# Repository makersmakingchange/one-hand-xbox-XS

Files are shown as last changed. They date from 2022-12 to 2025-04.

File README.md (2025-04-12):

<!--- Open Source Assistive Technology: GitHub Readme Template  --->

<!--- TITLE --->
 # One Handed Modification for Xbox Series X|S Controller

<!--- SUMMARY: A brief summary of the project. What it does, who it is for, how much it costs. --->
The one handed modification for the Xbox Series X|S Controller are modifications to allow users to operate an Xbox Series X|S controller with one hand. There are different modifications available for both right- and left-handed use.

The original design was created by [Akaki](https://www.printables.com/social/106360-akaki/about).

<!--- PHOTO --->
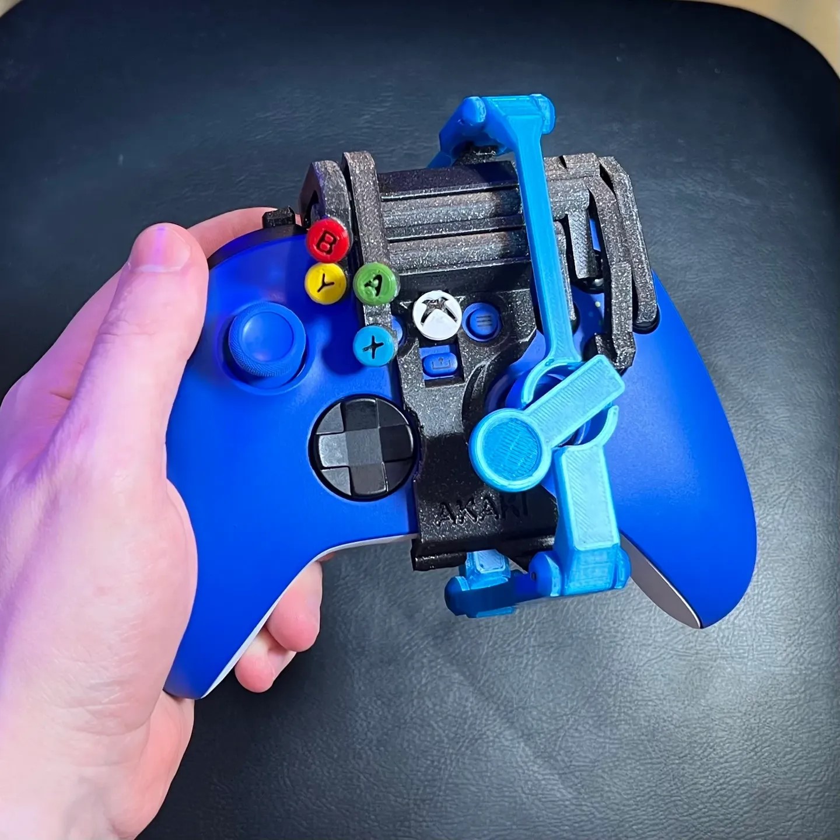
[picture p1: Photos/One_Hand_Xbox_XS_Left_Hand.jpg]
An Xbox controller with the left hand modification and Button Decorations being held in a left hand.
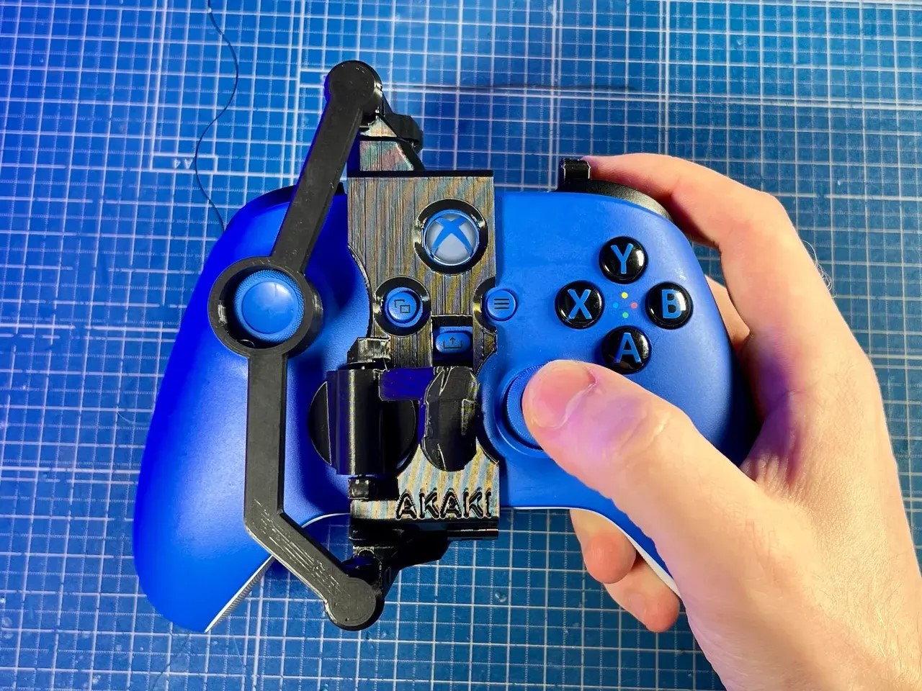
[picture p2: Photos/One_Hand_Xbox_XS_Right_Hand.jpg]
An Xbox controller with the right hand modification and Button Decorations being held in a right hand.
 

## More info at
 - [Makers Making Change Project Page](https://makersmakingchange.com/project/one-handed-mod-xbox-series-xs-controller)

## Getting Started
<!--- Include an overall idea of what major steps are required to build the device. --->

### 1. Order the Off-The-Shelf Components
The [Bill of Materials](/Documentation/OneHandedXboxXSController_BOM_V1.0.xlsx) lists all of the parts and components required to build the one handed modification for the Xbox Series X|S Controller.

### 2. Print the 3D Printable components
Select the correct modification (right or left handed modification) and print all the necessary parts for that modification.

All of the files and individual print files can be in the [/Build_Files/3D_Printing_Files](/Build_Files/3D_Printing/) folder.

### 3. Assemble the one handed modification for the Xbox Series X|S Controller.
Reference the [maker guide](/Documentation/OneHandedXboxXSController_Maker_Guide_V1.0.pdf) for the tools and steps required to build each portion.

<!---FILES: This section includes all the information and files required to build and modify the device, including documentation, design files, and build files. --->
## Files

<!--- DOCUMENTATION --->
### Documentation

| Document | Version | Link |
|----------|---------|------|
| Design Summary| 1.0 | [OneHandedXboxXSController_Summary](/Documentation/OneHandedXboxXSController_Summary.pdf) |
| Design Rationale     | 1.0 | [OneHandedXboxXSController_Design_Rationale](/Documentation/OneHandedXboxXSController_Design_Rationale.pdf) |
| Bill of Materials    | 1.0 | [OneHandedXboxXSController_BOM](/Documentation/OneHandedXboxXSController_BOM.xlsx) |
| Maker Guide      | 1.0 | [OneHandedXboxXSController_Maker_Guide](/Documentation/OneHandedXboxXSController_Maker_Guide.pdf) |
| User Guide          | 1.0 | [OneHandedXboxXSController_User_Guide](/Documentation/OneHandedXboxXSController_User_Guide.pdf)           |
| Changelog            | 1.0 | [OneHandedXboxXSController_Changelog](/Documentation/OneHandedXboxXSController_Changelog.pdf)               |

### Design Files
 - Unfortunately, no CAD files are available for this device.

### Build Files
<!--- BUILD FILES --->
 - [3D Printing Files](/Build_Files/3D_Printing)

## License
<!--- LICENSE: Choose an appropriate license. We recommend an open-source hardware compatible license. --->
Everything needed or used to design, make, test, or prepare the one handed modification for the Xbox Series X|S Controller is licensed under a Creative Commons Attribution-ShareAlike 4.0 license <https://creativecommons.org/licenses/by-sa/4.0/> (CC BY-SA 4.0).

Accompanying material such as instruction manuals, videos, and other copyrightable works that are useful but not necessary to design, make, test, or prepare the one handed modification for the Xbox Series X|S Controller are published under a Creative Commons Attribution-ShareAlike 4.0 license <https://creativecommons.org/licenses/by-sa/4.0/> (CC BY-SA 4.0).

## Attribution
<!--- ATTRIBUTION: Include any information related to the development of the design. This may include who identified the initial challenge, who contributed to the design --->

 - The original design of the [One-Handed Xbox Series XS Controller](https://www.printables.com/model/156112-one-handed-xbox-series-xs-controller) was created by [Akaki](https://www.printables.com/social/106360-akaki/about) and released with a [CC-BY-NC-SA license](http://creativecommons.org/licenses/by-nc-sa/4.0/).

 - The left handed modification was remixed by [Ryan Heitanen](https://www.printables.com/social/120065-ryan-hietanen/about).

 - Additional documentation was created by Neil Squire Society / Makers Making Change.
 - The documentation template was created by Makers Making Change and is used under a CC BY-SA 4.0 license. It is available at the following link: https://github.com/makersmakingchange/OpenAT-Template

----

<!-- ABOUT MMC START -->
## About Makers Making Change
[Makers Making Change Logo](https://www.makersmakingchange.com/)

Makers Making Change is a program of [Neil Squire](https://www.neilsquire.ca/), a Canadian non-profit that uses technology, knowledge, and passion to empower people with disabilities.

Makers Making Change leverages the capacity of community based Makers, Disability Professionals and Volunteers to develop and deliver affordable Open Source Assistive Technologies.

 - Website: [www.MakersMakingChange.com](https://www.makersmakingchange.com/)
 - GitHub: [makersmakingchange](https://github.com/makersmakingchange)
 - Bluesky: [@makersmakingchange.bsky.social](https://bsky.app/profile/makersmakingchange.bsky.social)
 - Instagram: [@makersmakingchange](https://www.instagram.com/makersmakingchange)
 - Facebook: [makersmakechange](https://www.facebook.com/makersmakechange)
 - LinkedIn: [Neil Squire Society](https://www.linkedin.com/company/neil-squire-society/)
 - Thingiverse: [makersmakingchange](https://www.thingiverse.com/makersmakingchange/about)
 - Printables: [MakersMakingChange](https://www.printables.com/@MakersMakingChange)

### Contact Us
For technical questions, to get involved, or to share your experience we encourage you to [visit our website](https://www.makersmakingchange.com/) or [contact us](https://www.makersmakingchange.com/s/contact).
<!-- ABOUT MMC END -->

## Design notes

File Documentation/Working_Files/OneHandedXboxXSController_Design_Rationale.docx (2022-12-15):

# Introduction

The One Handed Modification for the Xbox Series X|S Controller is a 3D-printed device that allows users to work an Xbox Series X|S with only one hand. This device may benefit users with only one hand, or limited mobility/dexterity in one of their hands. The device will fit Xbox Series X|S controllers.

# Research

## Xbox Adaptive Controller

The Xbox Adaptive Controller (XAC) allows players with limited mobility to customize their gaming setup for the Xbox with different switches and joysticks. Users can customize the XAC to map various functions to different switches, buttons, and joysticks to suit their needs. Although this option may be preferable for some users, it is expensive and requires users to purchase and customize other devices to use properly.

## One Handed Controller Modifications

There are one handed controller modifications available for purchase or DIY. Commercially available modified controllers are typically permanently modified and more expensive than standard controllers. Other DIY options may be difficult for makers and users to create and customize.

# Requirements

## Goals

G01 | Allow people to effectively use an Xbox Series X|S controller with one hand.
G02 | Help people with one hand and/or limited mobility/dexterity in one hand play video games.

## Functional Requirements

F01 | Must fit Xbox Series X|S controllers.
F02 | Must allow players to use the controller with one hand.

## Non-functional Requirement

NF01 | Must be easy to clean.

## Constraints

C01 | Must be printable on standard maker 3D printers.

# Version 1.0

Initial designs by Akaki (https://www.printables.com/social/106360-akaki/about) and Ryan Hietanen (https://www.printables.com/social/120065-ryan-hietanen/about) are licensed under Creative Commons (4.0 International License) Attribution – Non-Commercial – Share Alike (https://creativecommons.org/licenses/by-nc-sa/4.0/).

## Right handed version 1.0

This design consists of a single .stl file that contains multiple parts. The parts are listed below:

- Thumb-stick mover
- Linkage pieces
- Leg strap/shoe holder
- Mount
- Trigger button pusher
- D-pad pusher
- Leg strap attachment

## Left handed version 1.0

This design consists of a single .stl file that contains multiple parts. The parts are listed below:

- Thumb-stick mover
- Linkage pieces
- Leg strap/shoe holder
- Mount
- Trigger button pushers
- Face button pushers
- Leg strap attachment

## Optional Parts

The below parts are optional and can be found in their own .stl files.

- Shoe (replaces leg mount)
- Button decorations

# Opportunities for Improvement

- Add a cutout to allow users to easily access the USB-C power port at the back of the controller while using the device
- Split .stl files out into individual components to facilitate replacing parts or printing parts in different colours

© 2022 by Neil Squire. This work is licensed under the CC BY SA 4.0 License: http://creativecommons.org/licenses/by-sa/4.0 Files available at https://makersmakingchange.com/project/one-handed-mod-xbox-series-xs-controller Page 1 of 1

V1.0 | December 2022 One Handed Modification for The Xbox Series X|S Controller Design Rationale

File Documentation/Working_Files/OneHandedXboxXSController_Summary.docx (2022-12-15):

# Title

One Handed Modification for the Xbox Series X|S Controller

## Subtitle

The one handed modification for the Xbox Series X|S Controller are modifications to allow users to operate an Xbox Series X|S controller with one hand. There are modifications for the right and left hands.

## Device Specifications

Build Time:

< 1hr

1-4 hr

5-10hr

>10hr

Cost:

$0 - $10

$11 - $25

$26 - $50

$51 - $100

$101 - $250

$250+

Stage: Recently Added

Skills: 3D printing

Need: Agility/Dexterity

Disability: Mobility/Physical

Difficulty: Beginner

License: Attribution – Non-commercial – Share Alike 4.0 International

Usages: Recreation and Leisure

Type: Gaming

Designer: Akaki (https://www.printables.com/social/106360-akaki/about)

Left handed design remixed by: Ryan Hietanen (https://www.printables.com/social/120065-ryan-hietanen/about)

## Device Details

### Overview

This inexpensive 3D printed modification for the Xbox Series X|S controller will allow for the user to operate their Xbox Series X|S controller with one hand. This controller adaptation makes it easier for someone who may have a difficult time holding a controller with both hands, or has greater dexterity with one hand than the other.

### Usage

This controller adaptation allows for the user to operate their Xbox Series X|S controller with only one hand. For a left handed controller, the right joystick is used by moving the whole controller. By moving the controller, the 3D printed parts enable the joystick to move simultaneously. In addition, the right shoulder buttons are migrated to the left side so all four shoulder buttons can be used with the index finger. Similarly, four 3D printed arms are used to allow the user to press the A, B, X, Y, and home buttons from the left side.

There are two different attachments for the bottom of the controller shown below that can be used depending on whether the user chooses to strap the controller to their leg (right), or can rest it on their lap or a surface of their choice using the "shoe" (left).

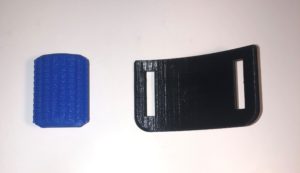
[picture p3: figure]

### Cost

The right handed modification costs $2.65 to produce and the left handed modification costs $3.00.

### Build Instructions

A set of instructions for creating this modification for the Xbox Series X|S controller can be found on the Prusa Printers website. There is a video tutorial showing the assembly of both the right and left handed versions linked here (https://www.youtube.com/watch?v=QOOU2KnhcHA).

The Xbox Series X|S controller is asymmetrical, so this modification has different files for the left and right handed modifications.

#### Skills Required

3D printing.

#### Time Required

3D printing time:

Right handed modification: 8.75-9.95 hours

Left handed modification: 10.9-12.2 hours

Assembly: 0.5-1.5 hours

#### Tools

- Flush cutters or scissors
- Sandpaper (optional)
- Superglue (optional)
- Drill and 5/64” drill bit (optional)

#### Components

- Rubber bands (optional)
- 1.75 mm 3D printer filament for pin joints

#### 3D Printing

Right Handed Modification | Left Handed Modification
Thumb-stick mover armature | Thumb-stick mover armature
Trigger pusher | Trigger pusher
Leg strap attachment | Leg strap attachment
Linkage pieces | Linkage pieces
Leg strap/shoe holder | Leg strap/shoe holder
D-pad pusher | B, A, X, Y face button pushers
Mount | Mount
Shoe (optional) | Shoe (optional)
Button decorations (optional) | Button decorations (optional)

### Design

### Attribution

Original design: Akaki (https://www.printables.com/social/106360-akaki/about)

Left handed design remixed by: Ryan Hietanen (https://www.printables.com/social/120065-ryan-hietanen/about)

© 2022 by Neil Squire. This work is licensed under the CC BY SA 4.0 License: http://creativecommons.org/licenses/by-sa/4.0 Files available at https://makersmakingchange.com/project/one-handed-mod-xbox-series-xs-controller Page 1 of 2

V1.0 | December 2022 One Handed Modification for The Xbox Series X|S Controller Summary

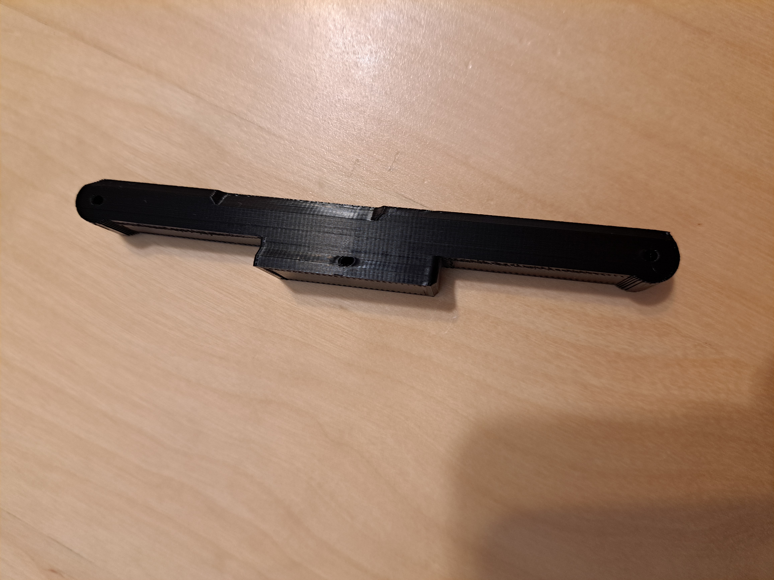
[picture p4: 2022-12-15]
Photos/right handed modification/Holder first side.jpg

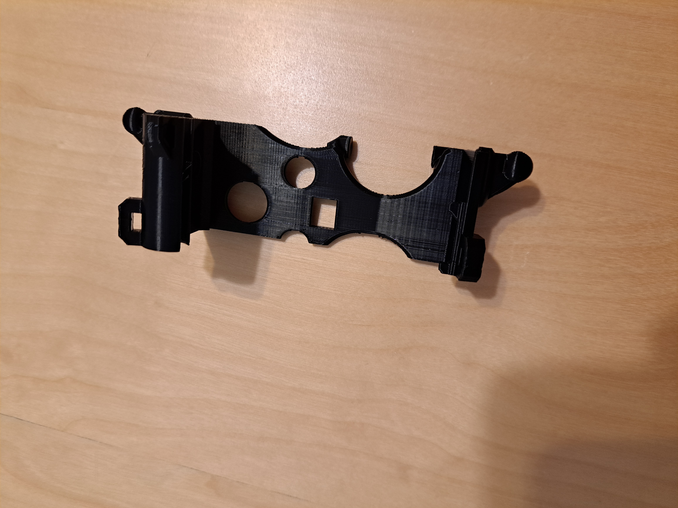
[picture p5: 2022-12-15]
Photos/right handed modification/Mount bottom.jpg

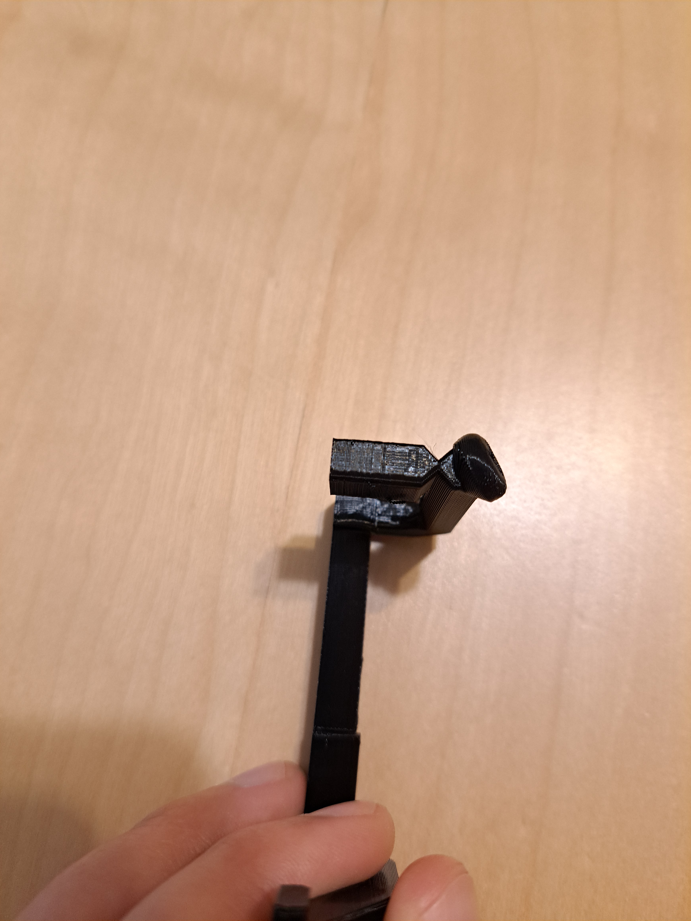
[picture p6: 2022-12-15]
Photos/left handed modification/A Button front.jpg

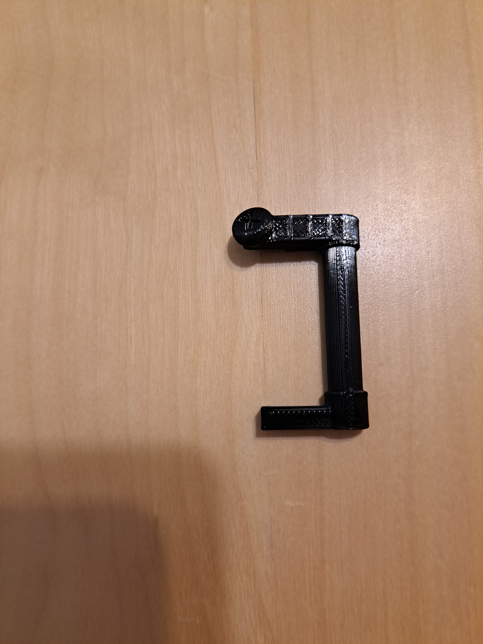
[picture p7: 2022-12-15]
Photos/left handed modification/X Button top.jpg

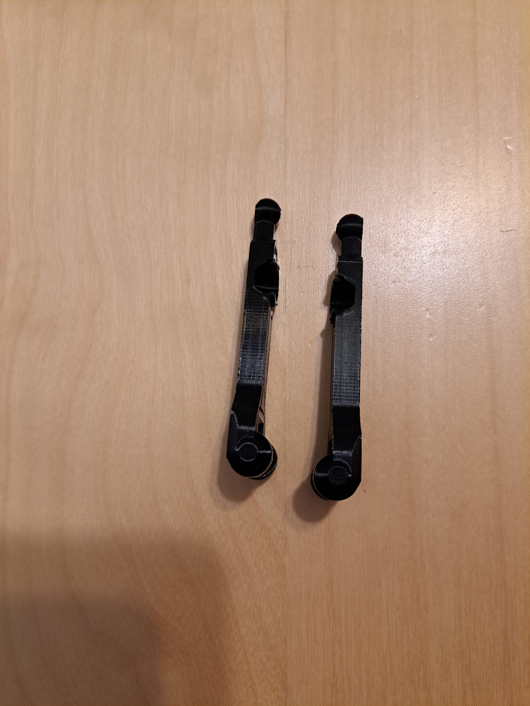
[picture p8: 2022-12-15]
Photos/right handed modification/Linkages side.jpg

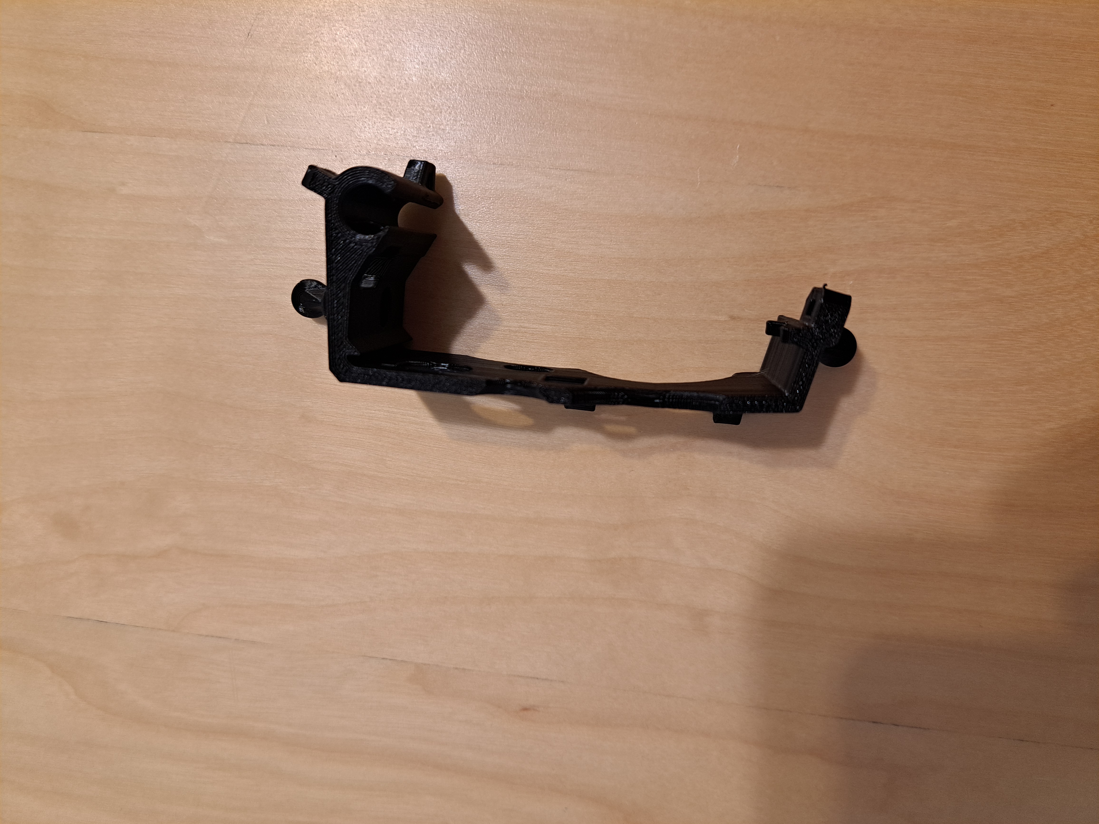
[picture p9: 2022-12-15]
Photos/right handed modification/Mount first side.jpg

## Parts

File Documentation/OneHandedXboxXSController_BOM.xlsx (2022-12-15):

Device: One Handed Modification for the Xbox Series X|S Controller |  |  | Total Cost | Total Print time (hr) | Total filament (g)
Version: V1.0 | Date Created: 11/20/2022 | Right handed | $2.65 | 9.95 | 64
Commercial Parts: |  | Left Handed | $3.00 | 12.20 | 78
Part type (Electrical. Mechanical, Sanitization, ect) | Part Name | Quantity Needed | Pkg Quantity | Price per package | Price per Unit | Price for qty needed | Link
Mechanical | Rubber bands (optional) | 5 | 600 | $13.99 | $0.02 | $0.12 | https://www.amazon.ca/stores/page/89A25064-42E4-458E-873D-0079F105D03D/?store_ref=SB_A0645920QPZJJP4FNBW2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
Mechanical | Hook and loop strap | 1 | 16 | $14.99 | $0.94 | $0.94 | https://www.amazon.ca/TamBee-Organizer-Reusable-Adjustable-Fastener/dp/B0B77CNTPH?hvadid=620922523376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
3D Printed Parts ESTIMATED PRICING USING 1KG ROLL COST: | $25.00
Part | Description | Quantity Needed | TOTAL Mass (g) | Estimated Price | Print Time (Min) | Link
Right handed modification | Right hand uses the controller | 1 | 55 | $1.38 | 525
Left handed modification | Left hand uses controller | 1 | 68 | $1.70 | 656
Button decorations (optional for Left handed modification, not used for right handed modification) | Make A, B, X, Y, and Xbox buttons different colour | 1 | 1 | $0.03 | 4
Shoe (optional) | Replaces leg strap | 1 | 9 | $0.22 | 72
 |  |  |  | $0.00
 |  |  | Total Print Cost: | $3.33
Tools for Assembly
1.75 mm 3D printer filament for pinned joints
Flush cutters
5/64" drill bit (optional)
Drill (optional)
Alternatives (if there are other sources for some parts link them below)
Part and description | Link

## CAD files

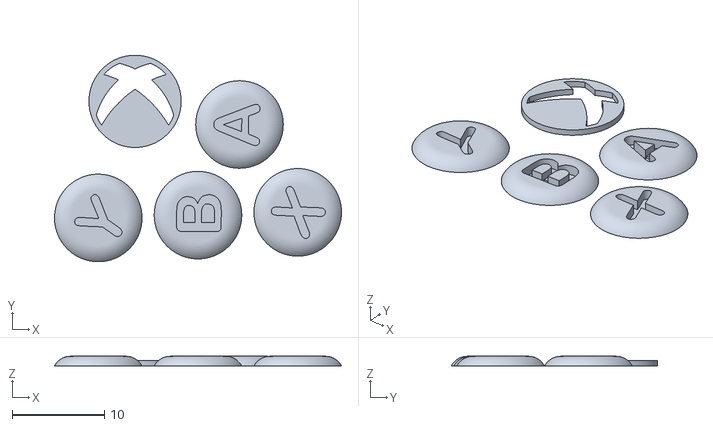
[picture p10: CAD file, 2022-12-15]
Build_Files/3D_Printing_Files/button decorations.stl
31.1 x 22.4 x 1.04

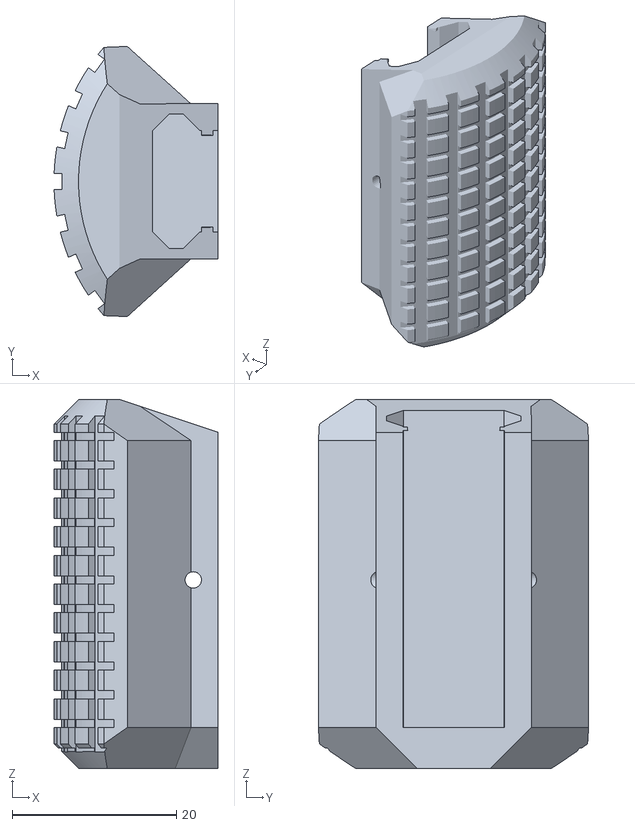
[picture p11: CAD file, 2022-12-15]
Build_Files/3D_Printing_Files/shoe.stl
20.0 x 33.0 x 45.0

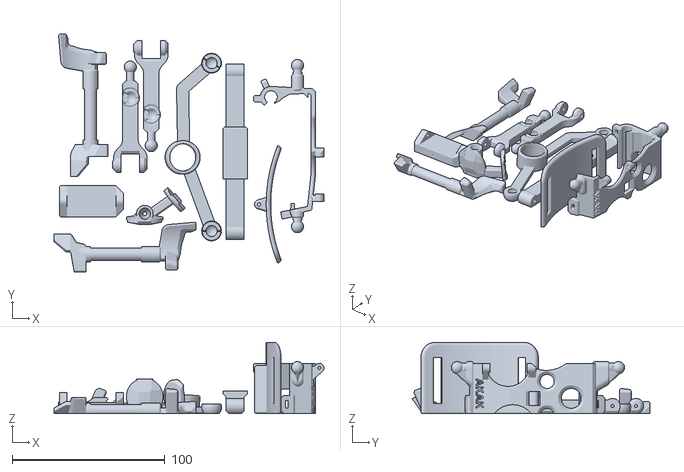
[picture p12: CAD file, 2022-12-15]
Build_Files/3D_Printing_Files/right handed xbox v1.stl
177.0 x 155.8 x 46.8

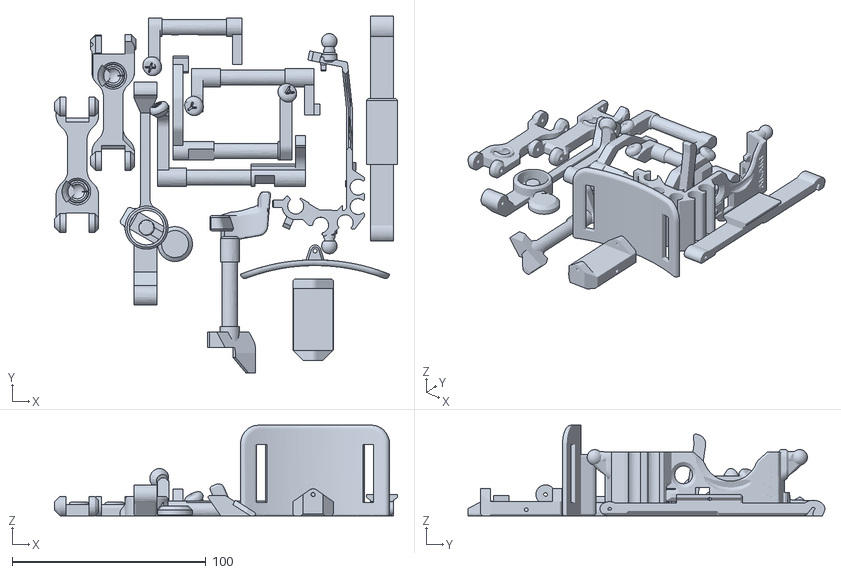
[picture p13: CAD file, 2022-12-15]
Build_Files/3D_Printing_Files/left-handed-xbox-Series X_S controller.stl
176.8 x 183.9 x 46.8

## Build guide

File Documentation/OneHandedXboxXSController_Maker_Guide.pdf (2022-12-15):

V1.0 | December 2022

# One Handed Modification for the Xbox Series X|S Controller

## MAKER GUIDE

© 2022 by Neil Squire (https://www.neilsquire.ca/)
This work is licensed under the CC BY SA 4.0 License: http://creativecommons.org/licenses/by-sa/4.0 Files available at https://makersmakingchange.com/project/one-handed-mod-xbox-series-xs-controller

### Overview

This document contains the necessary information to build a one handed modification for the Xbox Series X|S Controller.

### Contents

Step 1 | Error! Bookmark not defined.
Step 2 | Error! Bookmark not defined.
Step 3 | Error! Bookmark not defined.

# One Handed Modification for the Xbox Series X|S Controller

## MAKER GUIDE

© 2022 by Neil Squire (https://www.neilsquire.ca/)

### Maker Checklist

This list provides an overview of the steps required to build and deliver the device.

### Maker To Do List

Read through the Assembly Guide to become familiar with required components, tools, supplies, and safety gear and overall assembly steps.
Talk to User about customization options (e.g., colour, shoe vs leg strap, hook and loop strap size, etc.)
Gather tools, supplies, and safety equipment.
Assemble the device
Test device
Print “User Quick Guide”

### Items to Give to User

Assembled, tested device
“User Quick Guide”

### Tool List

Flush cutters or scissors
Sandpaper (optional)
Superglue (optional)
Drill and 5/64” drill bit (optional)

# One Handed Modification for the Xbox Series X|S Controller

## MAKER GUIDE

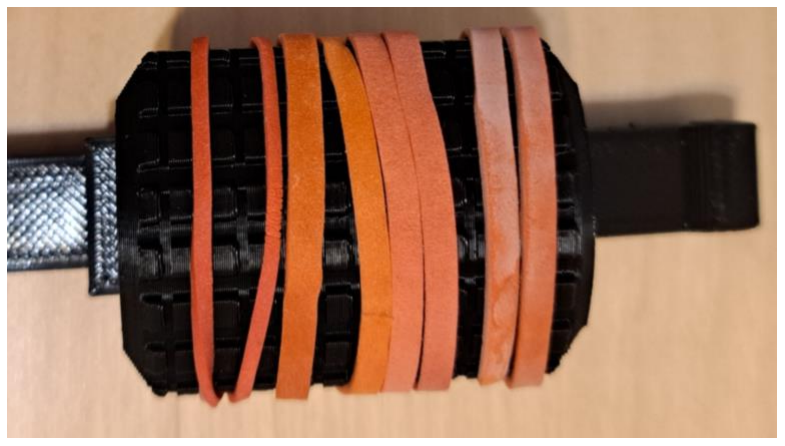
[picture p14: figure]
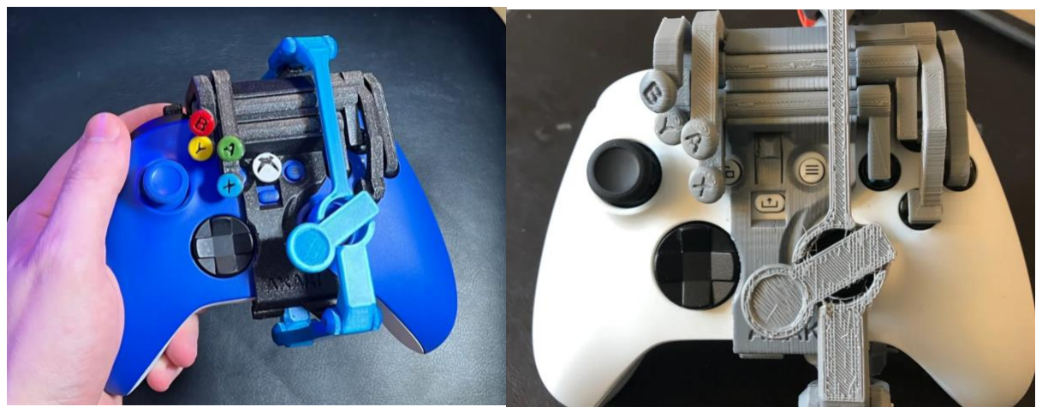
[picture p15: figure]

© 2022 by Neil Squire (https://www.neilsquire.ca/)

### Customization Guide

The user may request the “shoe” or leg strap for controlling the joystick of the unused hand. If the user requests the “shoe”, the original designer recommends printing it with TPU is possible. If printing in TPU is not possible, we recommend adding rubber bands around the “shoe” to increase grip, as shown below.

If the user requests the left handed modification, you may add the Button Decorations, ideally in a different colour from the rest of the device for colour contrast. The Button Decorations are a separate .slt file and include A, B, X, Y, and the Xbox logo. The controller with and without the Button Decorations is shown below.

# One Handed Modification for the Xbox Series X|S Controller

## MAKER GUIDE

© 2022 by Neil Squire (https://www.neilsquire.ca/)

### 3D Printing Guide

Note that all components can be printed without supports as the designer built supports into the design where necessary.

### 3D Printing Summary

Metrics | Right Handed Modification | Left Handed Modification | Button Decorations | Shoe
Total Print Time (min) | 525 (8.75 hours) | 656 (10.9 hours) | 4 (0.07 hours) | 72 (1.2 hours)
Total Number of Components | 10 | 12 | 5 | 1
Typical Total Mass (g) | 55 | 68 | <1 | 9
Typical Number of Print Setups | 1 | 1 | 1 | 1

### 3D Printing Settings

Print File Name | Qty | Total Print Time (hr:min) | Mass (g) | Infill (%) | Support(Y/N) | Layer Height/ Nozzle Diameter(mm) | Notes (orientation, special settings, etc.)
right handed xbox v1.stl | 1 | 8:45 | 55 | 20 | N | 0.2/0.4
left-handed-xbox-Series X_S controller.stl | 1 | 10:56 | 68 | 20 | N | 0.2/0.4
shoe.stl | 1 | 1:12 | 9 | 20 | N | 0.2/0.4 | -Optional print to replace leg strap - Can be printed in TPU if available
button decorations.stl | 1 | 0:04 | <1 | 20 | N | 0.2/0.4 | -Optional print

### Post-Processing

Remove any print helpers and built-in supports on the components.

# One Handed Modification for the Xbox Series X|S Controller

## MAKER GUIDE

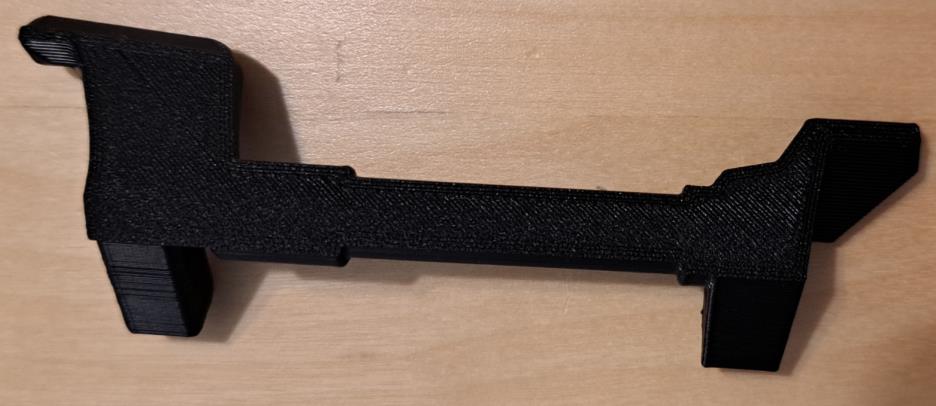
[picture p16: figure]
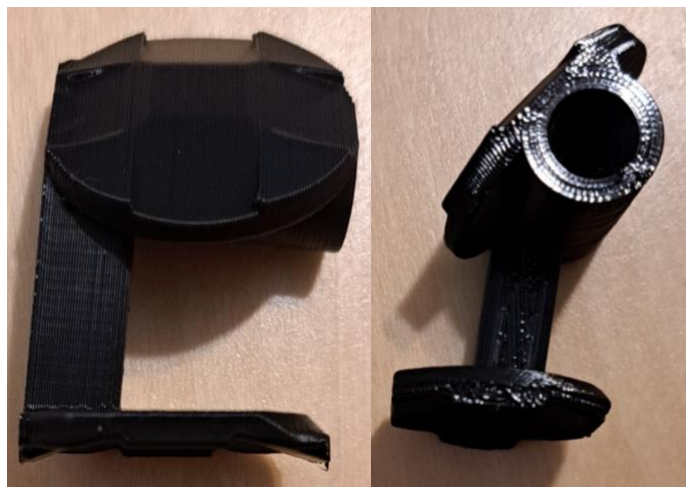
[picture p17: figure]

© 2022 by Neil Squire (https://www.neilsquire.ca/)

### Examples of Quality Prints

The following pictures show examples of quality prints for each component required for the controller modifications.

### Right Hand Modification

Trigger Pusher

D-Pad Pusher

# One Handed Modification for the Xbox Series X|S Controller

## MAKER GUIDE

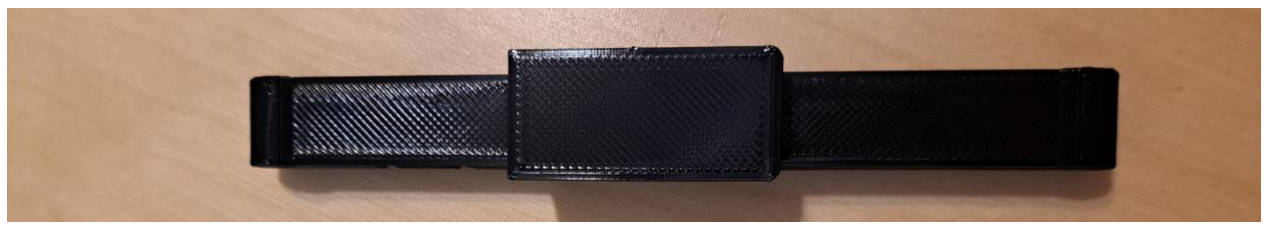
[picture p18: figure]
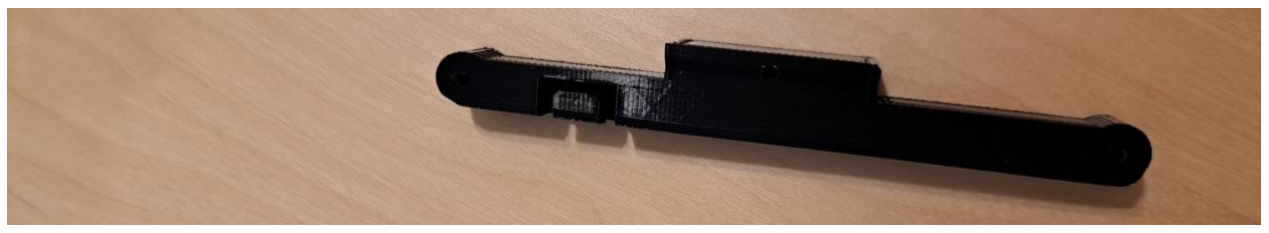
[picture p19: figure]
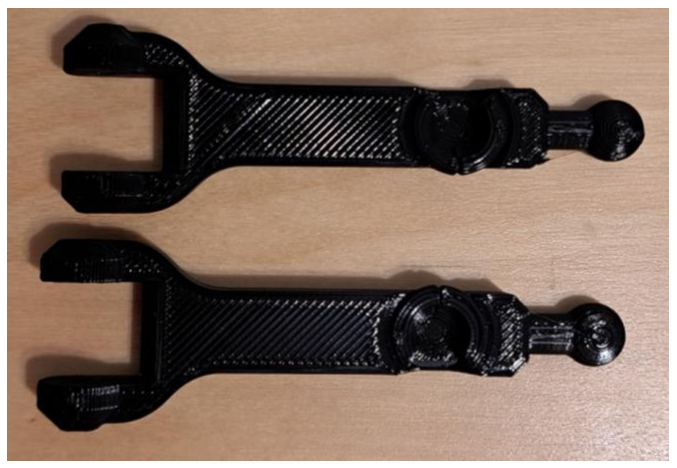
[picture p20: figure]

© 2022 by Neil Squire (https://www.neilsquire.ca/)

Leg Strap/Shoe holder

Linkage Pieces

# One Handed Modification for the Xbox Series X|S Controller

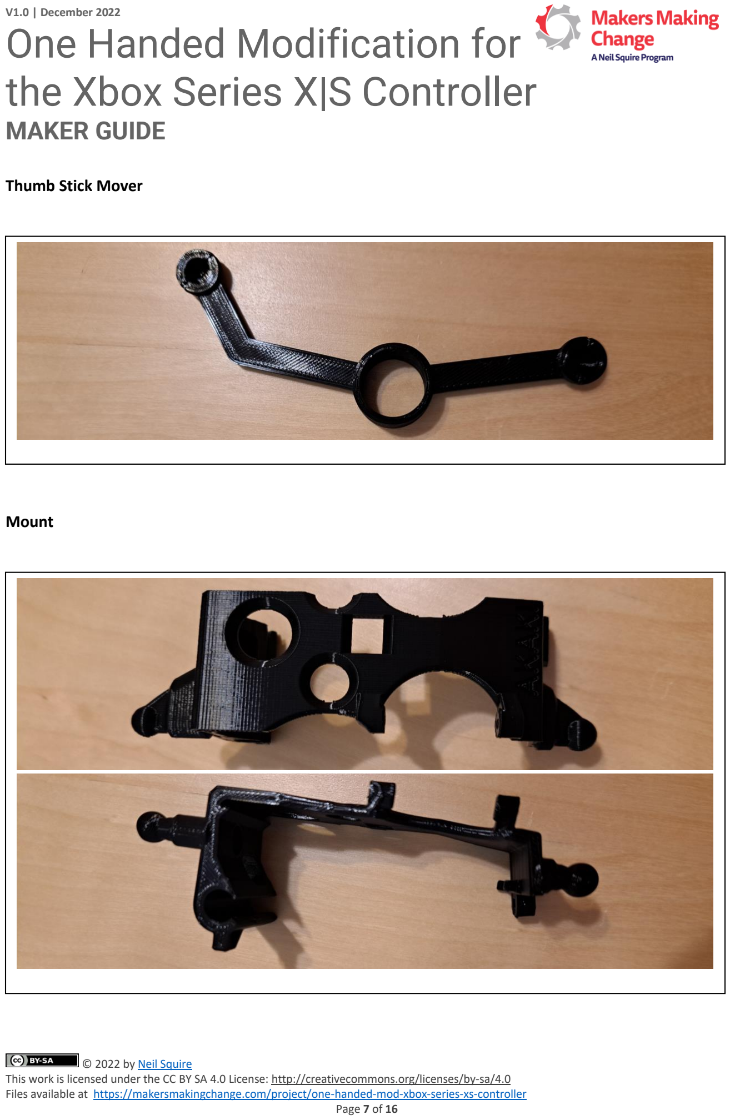
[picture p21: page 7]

## MAKER GUIDE

© 2022 by Neil Squire (https://www.neilsquire.ca/)

Thumb Stick Mover

Mount

# One Handed Modification for the Xbox Series X|S Controller

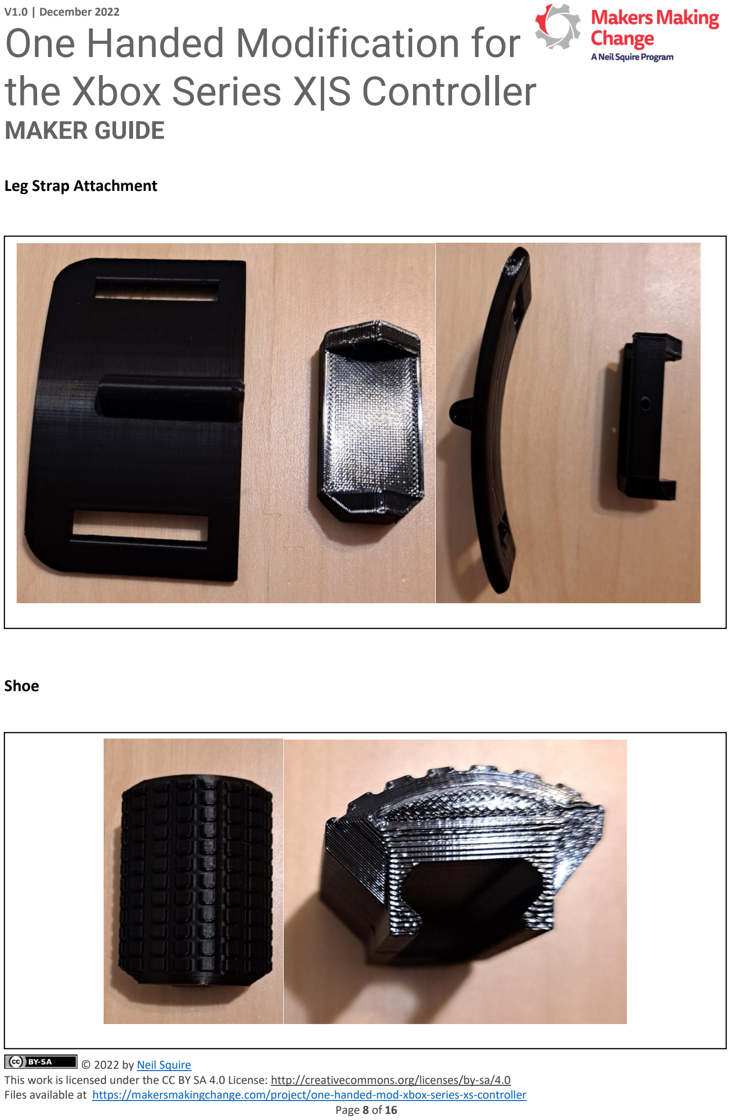
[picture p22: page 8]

## MAKER GUIDE

© 2022 by Neil Squire (https://www.neilsquire.ca/)

Leg Strap Attachment

Shoe

# One Handed Modification for the Xbox Series X|S Controller

## MAKER GUIDE

© 2022 by Neil Squire (https://www.neilsquire.ca/)

Button Decorations

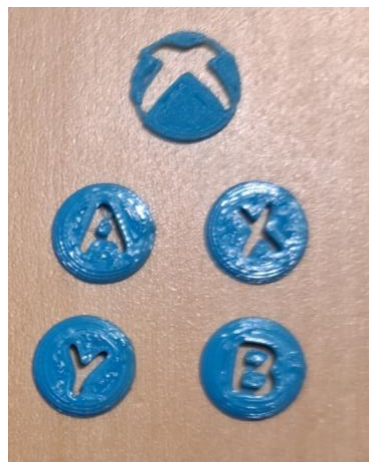
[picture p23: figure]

# One Handed Modification for the Xbox Series X|S Controller

## MAKER GUIDE

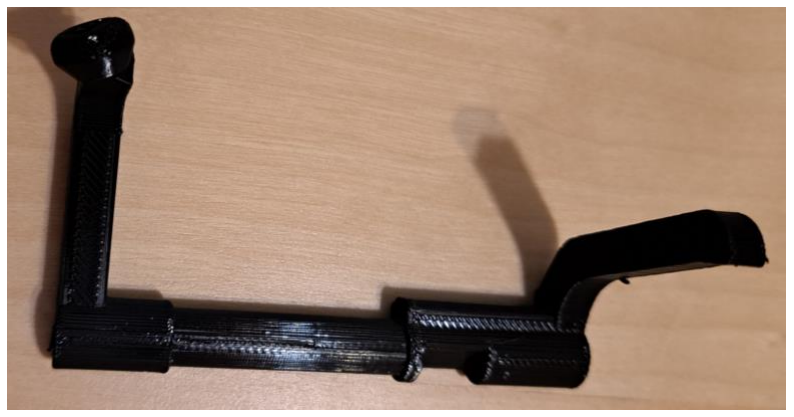
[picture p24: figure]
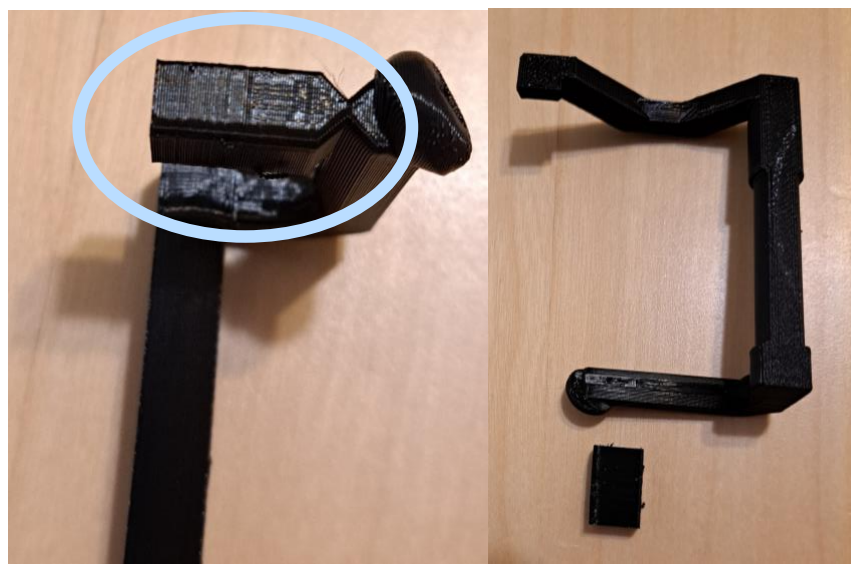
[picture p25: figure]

© 2022 by Neil Squire (https://www.neilsquire.ca/)

### Left Handed Modification

The left handed modification also includes the trigger pusher, leg strap/shoe holder, leg strap attachment/shoe, and optional button decorations. These parts are the same as those for the right handed modification.

B Button Pusher

A Button Pusher

# One Handed Modification for the Xbox Series X|S Controller

## MAKER GUIDE

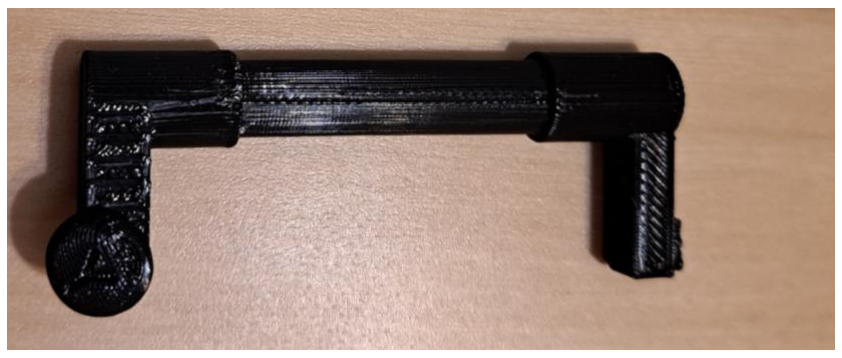
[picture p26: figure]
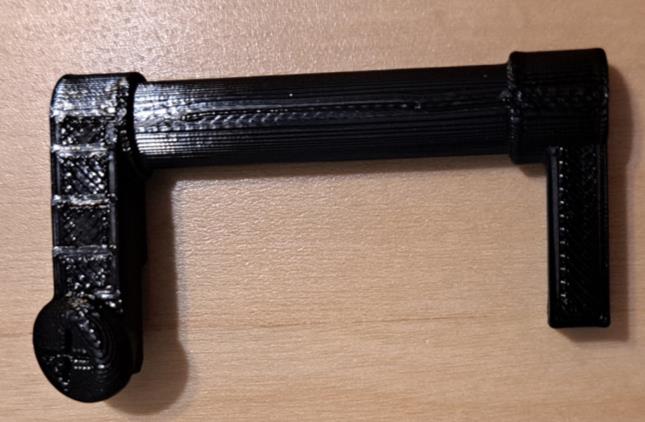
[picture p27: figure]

© 2022 by Neil Squire (https://www.neilsquire.ca/)

The A Button pusher has a built-in support, which is circled in the first picture. The support must be snapped off, and it comes off easily. The break should be clean, as seen in the last picture above.

Y Button Pusher

X Button Pusher

# One Handed Modification for the Xbox Series X|S Controller

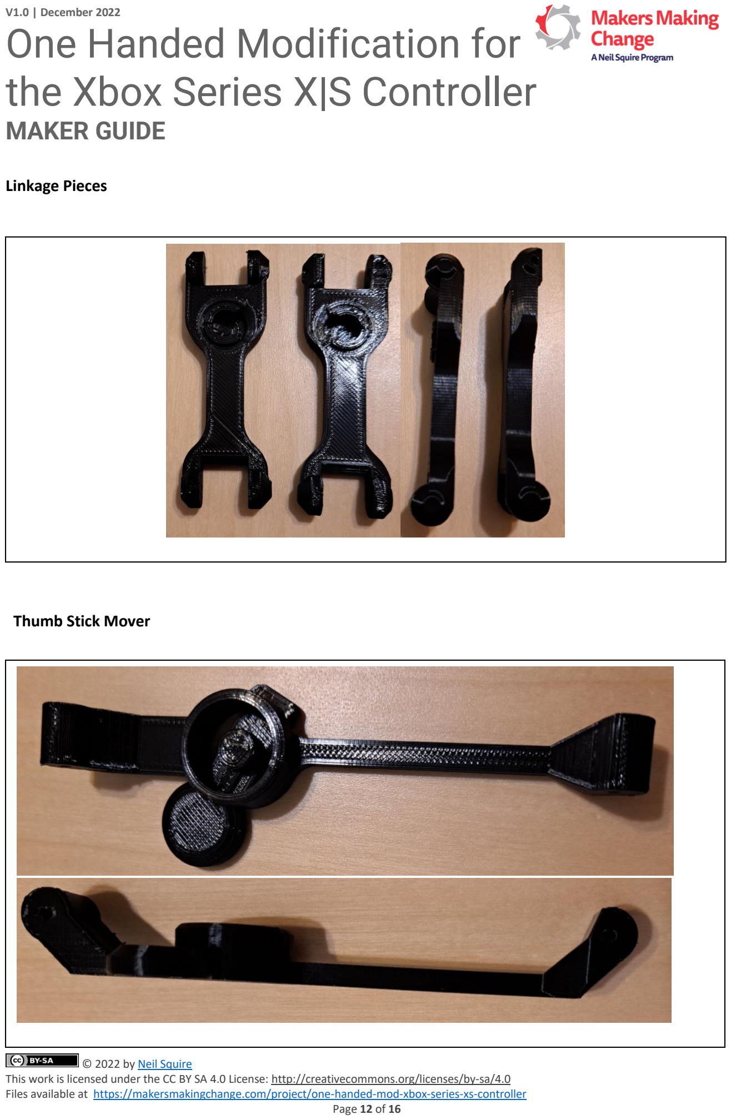
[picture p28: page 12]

## MAKER GUIDE

© 2022 by Neil Squire (https://www.neilsquire.ca/)

Linkage Pieces

Thumb Stick Mover

# One Handed Modification for the Xbox Series X|S Controller

## MAKER GUIDE

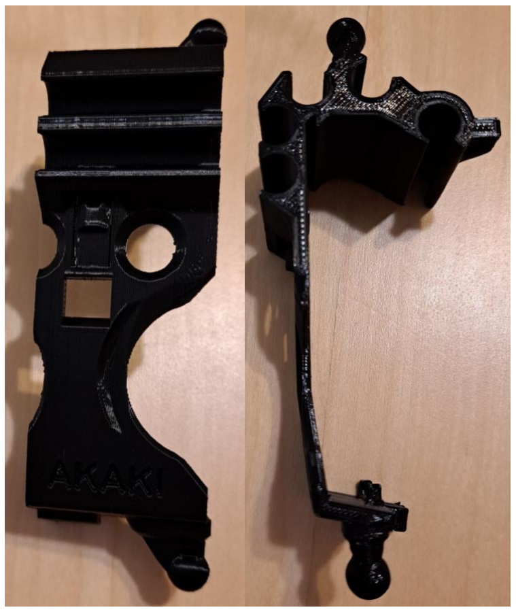
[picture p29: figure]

© 2022 by Neil Squire (https://www.neilsquire.ca/)

Mount

# One Handed Modification for the Xbox Series X|S Controller

## MAKER GUIDE

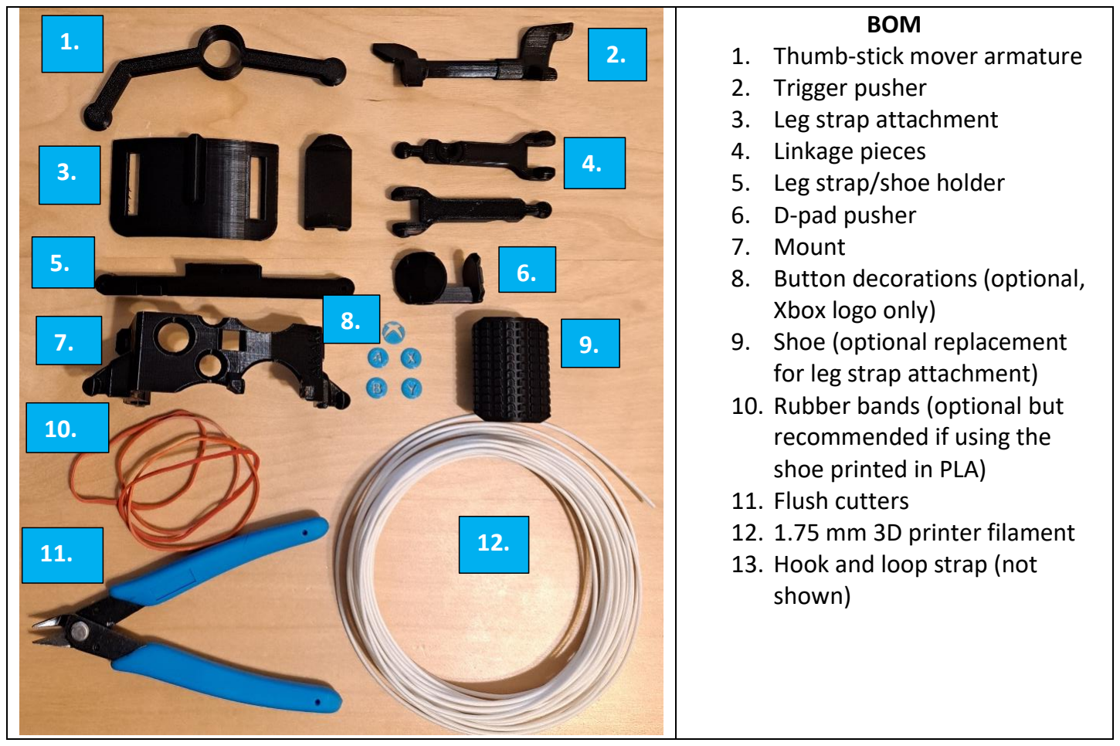
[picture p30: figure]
BOM 1. Thumb-stick mover armature 2. Trigger pusher 3. Leg strap attachment 4. Linkage pieces 5. Leg strap/shoe holder 6. D-pad pusher 7. Mount 8. Button decorations (optional, Xbox logo only) 9. Shoe (optional replacement for leg strap attachment) 10. Rubber bands (optional but recommended if using the shoe printed in PLA) 11. Flush cutters 12. 1.75 mm 3D printer filament 13. Hook and loop strap (not shown)

© 2022 by Neil Squire (https://www.neilsquire.ca/)

### Assembly Guide

### Required Components

Right Handed Modification

# One Handed Modification for the Xbox Series X|S Controller

## MAKER GUIDE

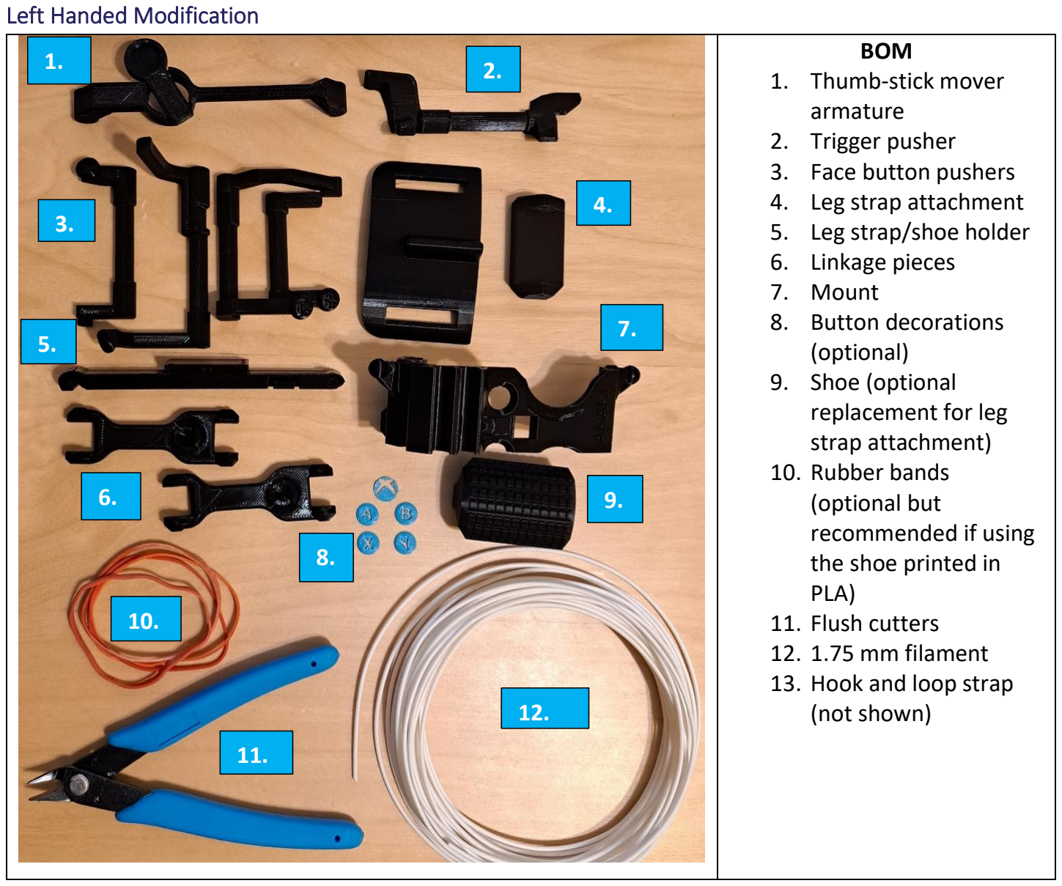
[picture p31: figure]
Left Handed Modification; BOM 1. Thumb-stick mover armature 2. Trigger pusher 3. Face button pushers 4. Leg strap attachment 5. Leg strap/shoe holder 6. Linkage pieces 7. Mount 8. Button decorations (optional) 9. Shoe (optional replacement for leg strap attachment) 10. Rubber bands (optional but recommended if using the shoe printed in PLA) 11. Flush cutters 12. 1.75 mm filament 13. Hook and loop strap (not shown)

© 2022 by Neil Squire (https://www.neilsquire.ca/)

### Required Tools

- Flush cutters/scissors
- Sandpaper (optional)
- Superglue (optional)

### Required Personal Protective Equipment (PPE)

- Safety glasses

# One Handed Modification for the Xbox Series X|S Controller

## MAKER GUIDE

© 2022 by Neil Squire (https://www.neilsquire.ca/)

### Assembly Instructions

See the original maker’s YouTube video (https://www.youtube.com/watch?v=QOOU2KnhcHA) for detailed assembly instructions. There are chapters in the video so you can skip ahead to the correct modification.

If the holes for the pinned connections are too tight for the 1.75mm filament, you can use a 5/64” drill bit to reshape/increase the size of the holes. The filament should still fit snugly but allow for easy rotation if you do so.

### Testing

Once the device is assembled, ensure all moving pieces move freely and don’t get stuck. If parts are getting stuck or are difficult to move, lightly sand the component until it moves freely. If you move a part multiple times you should start to see wear marks where the part is too tight. These wear marks will indicate the best place to sand. If you have an Xbox Series X|S controller, attach the device to the controller and test the movement. Make sure the button pushers don’t stick and everything moves freely.

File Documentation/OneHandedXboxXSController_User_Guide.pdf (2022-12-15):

V1.0 | December 2022

## One Handed Modification for the Xbox Series X|S Controller

## USER QUICK GUIDE

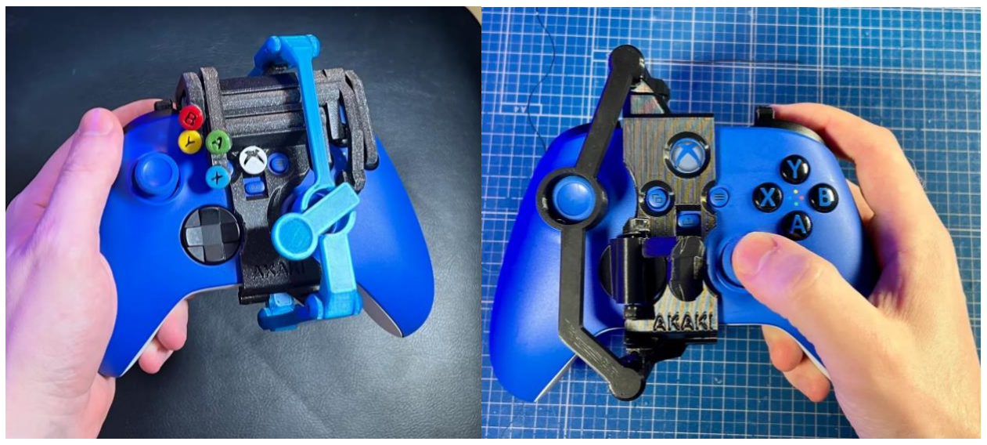
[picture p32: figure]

© 2022 by Neil Squire. (https://neilsquire.ca/)
This work is licensed under the CC BY SA 4.0 License: http://creativecommons.org/licenses/by-sa/4.0 Files available at https://makersmakingchange.com/project/one-handed-mod-xbox-series-xs-controller

### Introduction

The one handed modification for the Xbox Series X|S Controller are modifications to allow users to operate an Xbox Series X|S controller with one hand. There are modifications for the right and left hands.

### Features

### Usage

To attach the controller modification to the Xbox Series X|S controller, undo the ball joins on the thumbstick mover armature. Slide the mount onto the controller, starting at the bottom edge. Clip the mount entirely onto the controller; there should be an audible “click”, the mount should sit flush to the top of the controller, and it should be quite snug. If using the leg strap, strap the controller to your leg with the hook and loop fastener. If using the “shoe”, place the controller on your preferred surface. The modifications do not change the functionality of the Xbox controller; they allow the controller to be used with one hand.

### Compatibility

Note that the Xbox controllers can be used on PC based gaming and can be used with a Nintendo Switch with the correct adapter.

V1.0 | December 2022

## One Handed Modification for the Xbox Series X|S Controller

## USER QUICK GUIDE

© 2022 by Neil Squire. (https://neilsquire.ca/)
This work is licensed under the CC BY SA 4.0 License: http://creativecommons.org/licenses/by-sa/4.0 Files available at https://makersmakingchange.com/project/one-handed-mod-xbox-series-xs-controller

Platforms: Xbox Series X|S, Xbox One, PC, Nintendo Switch (with an adapter such as the one linked here). (https://www.amazon.ca/Mayflash-Magic-NS-Wireless-Controller-Nintendo/dp/B079B5KHWQ?hvadid=292937839648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)

Controllers: Xbox Series X|S Controllers (https://www.microsoft.com/en-ca/d/xbox-wireless-controller/8xn59crbsqgz)

### Specifications

Right handed modification:

Dimensions: 9.5 x 12 x 10 cm

Weight: 64 g

Left handed modifications:

Dimensions: 11.5 x 12 x 12 cm

Weight: 78 g

### Cleaning

The modifications can be disassembled and the pieces wiped clean with standard cleaners that do not destroy plastics.

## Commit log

2022-12-15 Revert "Delete OpenAT_Placard.stl"
    This reverts commit 0f3fbc9e3fd8c0f9f657a51064327dcd524d3c02.
    [OpenAT_Placard.stl]
2022-12-15 Created folders, uploaded files, and removed placeholder files.
    [DeviceName_BOM.xlsx, OneHandedXboxXSController_BOM.xlsx, OneHandedXboxXSController_BOM_V1.0.xlsx, button decorations.stl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]
2022-12-15 Delete OpenAT_Placard.f3d
    Do not have design files, only stl files for printing.
    [OpenAT_Placard.f3d]
2024-03-09 Delete Build_Files/3D_Printing_Files/OpenAT_Placard.stl
    Remove template file
    [OpenAT_Placard.stl]
2025-04-12 Remove version from documentation filenames
    [OneHandedXboxXSController_BOM.xlsx]
